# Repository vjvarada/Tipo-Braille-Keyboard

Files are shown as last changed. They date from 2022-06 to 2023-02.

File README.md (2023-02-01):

# What is a Braille KeyPad ?

- Braille KeyPad is a Bluetooth keyboard with a special layout that allows visually impaired individuals to easily navigate and type into SmartPhones and tablets. 
- There are 6 circular Braille input buttons on KeyPad arranged in a braille layout. By pressing combinations of the braille input buttons you can input text and symbols. Braille text input is compliant to UEB Grade 1 and Grade 2 braille except non-ASCII characters and some lower groupsigns & wordsigns.

# Physical Leyout:

- The braille keypads is a rectangular slab with rounded edges. It has all the buttons on one side, and is flat on the other.
- There is a slot for lanyard/wrist straps on one side of the rectangle. 
- Braille KeyPad consists of 6 circular "Braille" keys, 5 square "Special Keys" and a 5-Way Navigation stick with Center click.
- The 6 circular braille keys are used to input text and symbols by brailling in UEB grade 1 and grade 2 braille, in addition to long pressing the braille buttons of certain alphabets to trigger shortcuts on the SmartPhone/Tablet
- The 5 square keys are Alt, Ctrl, Shift, Space & Delete keys.
- The Navigation stick controls up, Down, Left, and Right.
- Clicking the center of the navigation stick represents enter/newline
- The bottom os the device has the ON/OFF slider and the USB Charging input.

# How to use
- Braille KeyPad is held between your palms, with the buttons facing away, and the flat side towards you. 

# Implementation:
How the HID Keypad is implemented for use with Braille

## Grade 1 Braille
The Braille Alphabet—Internationally Standardised
The letters a-z are common and standard for most braille country tables.

Grade 1 braille is a letter-for-letter substitution of its printed counterpart. This is the preferred code for beginners because it allows people to get familiar with, and recognize different aspects of, the code while learning how to read braille. 

English grade 1 braille consists of the 26 standard letters of the alphabet as well as punctuation.
### Charecters

| CHARACTER   |      BRAILLE      |  BRAILLE DOT/BUTTON # |
|----------|:-------------:|------:|
| letter sign | ⠰ | 56|
| a |	    ⠁	    | 1 |
| b |	    ⠃	    | 12 |
| c |	    ⠉	    | 14 |
| d |	    ⠙	    | 145 |
| e |	    ⠑	    | 15 |
| f |	    ⠋	    | 124 |
| g |	    ⠛	    | 1245 |
| h |	    ⠓	    | 125 |
| i |	    ⠊	    | 24 |
| j |	    ⠚	    | 245 |
| k |	    ⠅	    | 13 |
| l |	    ⠇	    | 123 |
| m |	    ⠍	    | 134 |
| n |	    ⠝	    | 1345 |
| o |	    ⠕	    | 135 |
| p |	    ⠏	    | 1234 |
| q |	    ⠟	    | 12345 |
| r |	    ⠗	    |1235 |
| s |	    ⠎	    | 234 |
| t |	    ⠞	    | 2345 |
| u |	    ⠥	    | 136 |
| v |	    ⠧	    | 1236 |
| w |	    ⠺	    | 2456 | 
| x |	    ⠭	    | 1346 |
| y |	    ⠽	    | 13456 |
| z |	    ⠵	    | 1356 |

### Numbers

| CHARACTER   |      BRAILLE      |  BRAILLE DOT/BUTTON # |
|----------|:-------------:|------:|
| number indicator |	⠼ 	| 3456 |
| 1 | 	⠼⠁	| 3456 1 |
| 2 |	⠼⠃	| 3456 12 |
| 3 |	⠼⠉	| 3456 14 |
| 4 |	⠼⠙	| 3456 145 |
| 5 |	⠼⠑	| 3456 15 |
| 6 |	⠼⠋	| 3456 124 |
| 7 |	⠼⠛	| 3456 1245 |
| 8 |	⠼⠓	| 3456 125 |
| 9 |	⠼⠊	| 3456 24 |
| 0 |	⠼⠚	| 3456 245 |

The number indicator (⠼) is placed before the first digit in a group. Space, hyphen, grade 1 indicator or clears it

Example:
```
100: 	⠼⠁⠚⠚

using Grade 1 indicator/Letter sign (⠰) to specify end of number
221b:	⠼⠃⠃⠁⠰⠃

```

### Punctuation

| CHARACTER   |      BRAILLE      |  BRAILLE DOT/BUTTON # |
|----------|:-------------:|------:|
|,|                     ⠂   |2|
|;|                  	⠆   |23|
|:|                    	⠒   |25|
|.(Period)|             ⠲   |256|
|?|     	            ⠦   |236|
|!|                     ⠖   |235|
|apostrophe '|          ⠄   |3|
|quote " |              ⠴   |356|
|hyphen - |             ⠤   |36|

### Symbols

| CHARACTER   |      BRAILLE      |  BRAILLE DOT/BUTTON # |
|----------|:-------------:|------:|
| & |	                 ⠈⠯	    | 4 12346|
| * |	                 ⠐⠔	    | 5 35|
| # |                    ⠸⠹        | 456 1456|
| @	|                    ⠈⠁        | 4 1|
| %	|                    ⠨⠴	    | 46 356|
| +	|                    ⠐⠖	    | 5 235|
| − (minus) |            ⠐⠤	    | 5 36|
| =	|                    ⠐⠶	    | 5 2356|
| ~ |                    ⠈⠔        | 4 35 |
| ` |                    ⠘⠡        | 45 16
| ^ |                    ⠈⠢        |4 26 |
| Underscore _ |         ⠨⠤        |46 36|
| Verical Line |         ⠸⠳        |456 1256| 
| / |                    ⠸⠌        |456 34|
| \ |                    ⠸⠡        |456 16|
| ( |                    ⠐⠣        |5 126|
| ) |                    ⠐⠜        |5 345|
| [ |                    ⠨⠣        |46 126|
| ] |                    ⠨⠜        |46 345|
| { |                    ⠸⠣        |456 126|
| } |                    ⠸⠜        |456 345|
| < |                    ⠈⠣        |4 126|
| > |                    ⠈⠜        |4 345|
| $ |                    ⠈⠎        |4 234 |
| " |                    ⠠⠶        |6 2346 |

### Indicators

| CHARACTER   |      BRAILLE      |  BRAILLE DOT/BUTTON # |
|----------|:-------------:|------:|
| number indicator |                	⠼    	| 3456 |
| grade 1 letter indicator |           ⠰	    | 56|
| grade 1 word indicator |             ⠰⠰	    | 56 56|
| grade 1 lock indicator |             ⠰⠰⠰	    | 56 56|
| grade 1 terminator indicator |       ⠰⠄	    | 56 3|
| capital letter indicator |           ⠠	    | 6|
| capital word indicator |             ⠠⠠      | 6 6|
| capital lock indicator |             ⠠⠠⠠     | 6 6 6|
| capital terminator indicator |       ⠠⠄      | 6 3|

```
The capital(ization) sign ⠠ marks the first letter of a word as capitalized. 
It may occur in the middle of a word for camel case, as in the name deAngelo. 
It is doubled to place a word in all caps; this must be repeated for each word of an all-cap text.
Use ⠠⠠ to Capitalise proceeding charecter, ⠠⠠ to Capitalise a full word,
⠠⠠⠠ to capitalise a full passage and ⠠⠄ to terminate. Using space/hyphen 
etc resets to normal unless not using paragraph caps. 
Warning: ⠠⠺⠁⠗⠝⠊⠝⠛
WARNING: ⠠⠠⠺⠁⠗⠝⠊⠝⠛
```

```
Note: The letter sign (grade 1 symbol indicator) ⠰ is used to force the end of a series of numbers.
For example, ⠙⠁ ⟨da⟩ preceded by a number sign, ⠼⠙⠁, is read as 41. 
If instead 4a is intended (as in a section or apartment number), 
then the letter sign is used to force a reading of a rather than 1 for the final character: ⠼⠙⠰⠁ ⟨4a⟩.

It is also used to mark a character as standing for a letter rather than for a word. For example, ⠃ ⟨b⟩ on its own is normally read as the word but;
to indicate that it is instead the letter b, the letter sign is used: ⠰⠃ b. Plurals of letters (mind your ps and qs)
always use an apostrophe in braille, but other derivations may not, as in ⠰⠝⠹ nth [time]: ⠠⠎⠬ is Sing, ⠰⠠⠎⠬ is S-ing/Essing. The letter sign is also used to mark lower-case Roman numbers, as in ⠰⠊⠊⠊ ⟨iii⟩.
 ```
## Grade 2 Braille 

The literary braille code, grade 2, uses “contractions” that substitute shorter sequences for the full spelling of commonly-occurring letter groups. The contractions are similar to English print contractions, like “cannot” versus “can’t”, in the way that a word is shortened. For example, “the” is usually a single character in braille. 
Grade 2 braille is the most commonly used form of braille code and is found in books, public signage, and restaurant menus to name a few. It consists of the 26 standard letters of the alphabet, punctuation, and contractions.

```
letter sign  (⠰) used to mark a character as standing for a letter rather than for a word. For example,
 ⠃ ⟨b⟩ on its own is normally read as the word but; to indicate that it is instead the letter b, 
the letter sign is used: ⠰⠃ b. Plurals of letters (mind your ps and qs) always use an apostrophe in braille,
but other derivations may not, as in ⠰⠝⠹ nth [time]: ⠠⠎⠬ is Sing, ⠰⠠⠎⠬ is S-ing/Essing.[27] The letter sign 
is also used to mark lower-case Roman numbers, as in ⠰⠊⠊⠊ ⟨iii⟩.
```
### Alphabetic Wordsigns

| CHARACTER   | WORD    |      BRAILLE      |  BRAILLE DOT/BUTTON # |
|----------|:-------------:|:-------------:|------:|
| b | but |	            ⠃	    | 12 |
| c | can |	            ⠉	    | 14 |
| d | do |	            ⠙	    | 145 |
| e | every|            ⠑	    | 15 |
| f | from |            ⠋	    | 124 |
| g | go |              ⠛	    | 1245 |
| h | have |            ⠓	    | 125 |
| j | just |            ⠚	    | 245 |
| k | knowledge |	    ⠅	    | 13 |
| l | like |	        ⠇	    | 123 |
| m | more |	        ⠍	    | 134 |
| n | not |	            ⠝	    | 1345 |
| p | people |	        ⠏	    | 1234 |
| q | quite |	        ⠟	    | 12345 |
| r | rather |	        ⠗	    |1235 |
| s | so |	            ⠎	    | 234 |
| t | that |	        ⠞	    | 2345 |
| u | us |	            ⠥	    | 136 |
| v | very |	        ⠧	    | 1236 |
| w | will |	        ⠺	    | 2456 | 
| x | it |	            ⠭	    | 1346 |
| y | you |	            ⠽	    | 13456 |
| z | as |	            ⠵	    | 1356 |

### Strong Contractions (Part and Whole Word)

| CHARACTER   |      BRAILLE      |  BRAILLE DOT/BUTTON # |
|----------|:-------------:|------:|
| and |	    ⠯	    | 12346 |
| for |	    ⠿	    | 123456 |
| of |	    ⠷	    | 12356 |
| the |	    ⠮	    | 2346 |
| with |    ⠾	    | 23456 |

### Strong Wordsigns

| CHARACTER   |      BRAILLE      |  BRAILLE DOT/BUTTON # |
|----------|:-------------:|------:|
| child |	    ⠡	    | 16 |
| shall |	    ⠩	    | 146 |
| this |	    ⠹	    | 1456 |
| which |	    ⠱	    | 156 |
| out |	        ⠳	    | 1256 |
| still |	    ⠌	    | 34 |

isStandingAlone?

### Strong Groupsigns

| CHARACTER   |      BRAILLE      |  BRAILLE DOT/BUTTON # | Note |
|----------|:-------------:|:------:|------:|
| -ch- |	    ⠡	    | 16 | Letter join on either side|
| -sh- |	    ⠩	    | 146 |Letter join on either side|
| -th- |        ⠹	    | 1456 |Letter join on either side|
| -wh- |	    ⠱	    | 156 |Letter join on either side|
| -ou- |	    ⠳	    | 1256 |Letter join on either side|
| -st- |	    ⠌	    | 34 |Letter join on either side|
|------|----------------|----| -------------------------|
| gh |	        ⠣	    | 126 |
| ed |	        ⠫	    | 1246 |
| er |	        ⠻	    | 12456 |
| ow |          ⠪	    | 246 |
| ar |  	    ⠜	    | 345 |
| -ing |	    ⠬	    | 346 |Letter join on one side only, cannot be used to start a word|

### Lower Groupsigns

| CHARACTER   |      BRAILLE      |  BRAILLE DOT/BUTTON # | Note |
|----------|:-------------:|:------:|------:|
| -ea- |      ⠂	    | 2|Letters join on both side|
| -bb- |      ⠆	    | 23 |Letters join on both side|
| -cc- |      ⠒	    | 25 |Letters join on both side|
| -ff- |	  ⠖	    | 235 |Letters join on both side|
| -gg- |      ⠶	    | 2356 |Letters join on both side|
|------|----------------|----| -------------------------|
| be- |	      ⠆	    | 23 | |
| con- |	  ⠒	    | 25 |Letters join on one side only |
| dis- |	  ⠲	    | 256 |Letters join on one side only |
| -en- |	  ⠢	    | 26 |Letter join on either side|
| in |	      ⠔	    | 35 | |

### Lower Wordsigns

| CHARACTER   |      BRAILLE      |  BRAILLE DOT/BUTTON # |
|----------|:-------------:|------:|
| be |      ⠆	    | 23 |
| enough |  ⠢	    | 26 |
| were |    ⠶	    | 2356 |
| his |	    ⠦	    | 236 |
| in |	    ⠔	    | 35 |
| was |	    ⠴	    | 356 |

### Initial Letter Contractions

| CHARACTER   |      BRAILLE      |  BRAILLE DOT/BUTTON # |
|----------|:-------------:|------:|
|    day |  |5 145
|   ever |  |5 15
|  father | |5 124
|    here | |5 125
|    know | |5 13
|    lord | |5 123
|    mother |   |5 134
|    name | |5 1345
|    one |  |5 135
|    part | |5 1234
|    question | |5 12345
|    right |    |5 1235
|    some | |5 234
|    time | |5 2345
|    under | |5 136
|    work | |5 2456
|    young | |5 13456
|    there | |5 2346
|    character | |5 16
|    through | |5 1456
|    where | |5 156
|    ought | |5 1256
|    upon | |45 136
|    word | |45 2456
|    these | |45 2346
|    those | |45 1456
|    whose | |45 156
|    cannot | |456 14
|    had | |456 125
|    many | |456 134
|    spirit | |456 234
|    world | |456 2456
|    their | |456 2346

### final Letter Groupsigns

| CHARACTER   |      BRAILLE      |  BRAILLE DOT/BUTTON # |
|----------|:-------------:|------:|
|ound| | 46 145 |
|ance| | 46 15 |
|sion| | 46 1345 |
|less| | 46 234|
|ount| | 46 2345|
|ence| | 56 15|
|ong| | 56 1245|
|ful| | 56 123|
|tion| | 56 1345|
|ness| | 56 234|
|ment| | 56 2345|
|ity| | 56 13456|

## Talkback Basics

|Key Combo      |   Action | 
|:----------|------:|
| Hold z | Pause/Resume Talkback | 
| Alt + Space | Open Talkback Menu | 

## Item Navigation controls

|Key Combo      |   Action | 
|:----------|------:|
| Alt + Left  | Navigate to the next item|
| Alt + Right  | Navigate to the previous item |
| Alt + Up | Navigate to the item above |
| Alt + Down | Navigate to the item below|
|_________|________|
| Alt + Ctrl + Left | Navigate to First Item |
| Alt + Ctrl + Right | Navigate to Last Item |
| Alt + Ctrl + Down  | Navigate to Next Window |
| Alt + Ctrl + Up | Navigate to Previous Window |
|_________|________|
| Alt + Enter | Select an item |
| Alt + Shift + Enter |Long press | 

## Text Editing  
|Key Combo      |   Action | 
|:----------|------:|
| Right | Move cursor right |
| Left | Move cursor left |
| Up | Move cursor to line above |
| Down | Move cursor to line below |
| Ctrl + Right | Move cursor to Previous Word |
| Ctrl + Left | Move Cursor to Next Word |
| Shift + Right | Select next character |
| Shift + Left | Select Previous Character |
| Shift + Up | Select Line Above |
| Shift + Down | Select Line Below |
| Shift + Ctrl + Left | Select Previous Word |
| Shift + Ctrl + Right | Select Next Word |

## Reading controls

|Key Combo      |   Action | 
|:----------|------:|
| Alt + Shift + Control + Up/Down | Cycle Reading Controls | 
| Alt + Shift + Up/Down | Go to Next/Prev as per reading Controls |
| Alt + Shift + Right  | Navigate to Next Character |
| Alt  + Shift + Left |  Navigate to Previous Character |
| Alt + Ctrl + Shift + Right | Navigate to Next Word |
| Alt + Ctrl + Shift + Left |  Navigate to Previous Word |

## Continuous Reading controls

|Key Combo      |   Action | 
|:----------|------:|
| Alt + Ctrl + Enter | Continuous read from top |
| Alt + Ctrl + Shift + Enter | Continuous read from Next Item |
| Alt + Right  | Fast-forwards the text.|
| Alt + Left | Rewinds the text. |
| Enter | Stop Continuous Reading |

## Slider Controls  

|Key Combo      |   Action | 
|:----------|------:|
| Alt + Shift + Up | Increase Slider Value|
| Alt + Shift + Down  | Decrease Slider Value |

## Alphabetic Shortcuts

Long press braille character to activate

| CHARACTER   |      Shortcut      |  Key Combo |
|----------|:-------------:|------:|
| a | Assistant | win |
| b | Back | alt + backspace |
| l | Apps List / Select All | Ctrl + a |
| c | Copy | ctrl + c |
| x | Cut | ctrl + x |
| v | Paste | ctrl + v |
| d | Maps | win + m |
| e | Email | win + e |
| h | Home | ctrl + alt + h |
| r | Recent apps | ctrl + alt + r |
| s | Music | win + p |
| m | Messages | win + s |
| n | notifications | ctrl + alt + n |
| f | Screen Search | ctrl + alt + / |
| p | Contacts | win + c |
| y | Youtube | win + y |
| t | Calender | win + l |

#### References:

1. Generate Markdwn tables from https://www.tablesgenerator.com/markdown_tables
2. Braille Code Referance: https://www.pharmabraille.com/braille-codes/unified-english-braille-ueb-code/
3. Test and understand using online braille translator: https://www.branah.com/braille-translator
4. Wikipedia entry https://en.wikipedia.org/wiki/English_Braille
5. http://www.dotlessbraille.org/brailleindicators.htm#markup
6. Android & TalkBack Mobile Accessibility Cheat Sheet https://pauljadam.com/demos/talkbackcheatsheet.html
7. Keyboard Shortcuts https://www.cnet.com/culture/keyboard-shortcuts-for-android-phones/
8. Talkback Shortcuts https://dequeuniversity.com/screenreaders/talkback-shortcuts
9. Braille to Binary encoder https://www.dcode.fr/braille-alphabet

# TIPO
Plug n Play Braille Keyboard for your smartphone
Shows up as a HID device, and behaves just like a Keyboard would.

## TIPO V1
USB HID only implementation using atmega32u4/Adruni Leonardo

## TIPO BLE

BLE HID implementation using ESP32

------------------------------------------------------------------
# Hardware Connections

## Architecture
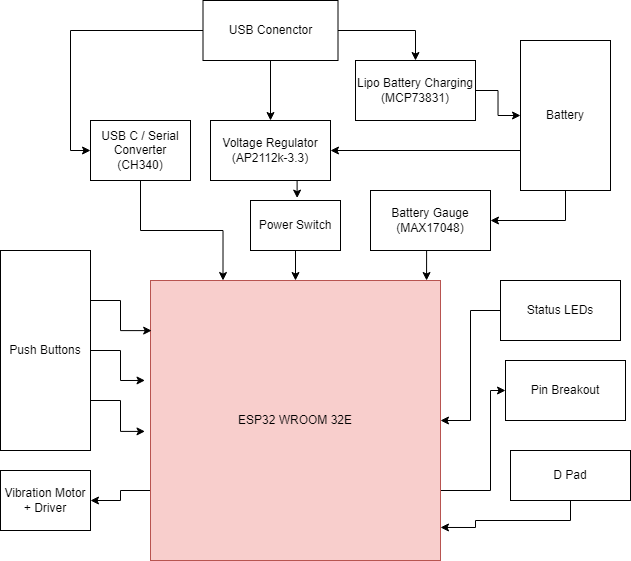
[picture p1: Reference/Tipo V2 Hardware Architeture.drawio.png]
Hardware Architecture


## Button Map:

| Button | ESP32 Pin # |
| :------: | :-----------:|
| BTN1 | 25|
| BTN2 | 26|
| BTN3 | 27|
| BTN4 | 13|
| BTN5 | 15|
| BTN6 | 2 |
| BTN7 | 19|
| BTN8 | 18|
| BTN9 | 17|
| BTN10| 16|
| BTN11| 4 |
| CNT | 33|
| UP | 34 |
| DWN | 35|
| LFT | 36|
| RGT | 39|

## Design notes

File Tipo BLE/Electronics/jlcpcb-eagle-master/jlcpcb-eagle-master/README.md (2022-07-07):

# jlcpcb-eagle
EAGLE cad helpers for JLCPCB (https://jlcpcb.com) production and assembly services

## General info

Rules and scripts have been tested under EAGLE cad 9.5.

They're provided AS IS, with no warranty. Any feedback is greatly appreciated and
can be provided via issue tickets.

### Installation

Copy each file in their respective folders (USER_HOME/Documents/EAGLE/).

## CAM jobs

The details of these CAM jobs are covered in article [How to Generate Gerber and Drill Files in Autodesk Eagle](https://support.jlcpcb.com/article/137-how-to-generate-gerber-and-drill-files-in-autodesk-eagle), so they must be used together.

The jobs follow the naming guidelines defined here: https://support.jlcpcb.com/article/29-suggested-naming-patterns

They also include tCream/bCream solderpaste layers that could be used for the stencil service.

### Eagle 8.6.0 to 9.6.2

* cam/jlcpcb_2_layer_v9.cam : For 2-layer boards
* cam/jlcpcb_4_layer_v9.cam : For 4-layer boards
* cam/jlcpcb_6_layer_v9.cam : For 6-layer boards

### Eagle 7.2 to 8.5.2

* cam/jlcpcb_2_layer_v72.cam : For 2-layer boards
* cam/jlcpcb_4_layer_v72.cam : For 4-layer boards
* cam/jlcpcb_6_layer_v72.cam : For 6-layer boards

### Eagle 7.1 and Lower

For Eagle 5, 6 and 7.1

* cam/jlcpcb_2_layer_v6.cam : For 2-layer boards
* cam/jlcpcb_4_layer_v6.cam : For 4-layer boards
* cam/jlcpcb_6_layer_v6.cam : For 6-layer boards

## Design rules

* design rules/jlcpcb-2layers.dru: 2-layers version, 35u copper, 1.6mm board thickness

Mainly based on EAGLE's standard design rules, it adds the declared JLCPCB's capabilities listed
here: https://jlcpcb.com/capabilities/Capabilities

Note: annular ring for pads aren't minimal, in order to allow proper solderability of TH components

## ULPs

### BOM/CPL Exporter

* BOM: Bill of Materials
* CPL: Component Placement List (i.e. Pick and Place file)

The smta exporter ULP can be used to quicken the process of creating the required files for the SMT assembly service.

#### Files

* ulps/jlcpcb_smta_exporter.ulp: For Eagle 9
* ulps/jlcpcb_smta_exporter_v7.ulp: Tested in Eagle 7.7.0

#### Usage

Observe the following:

1. it must be executed from the board editor
2. it asks for the layer to process (either top or bottom), this must be consistent with the ordering process
3. it asks for a directory where to export the two files
4. the two files will be named ```<boardname>_<side>_bom.csv``` and ```<boardname>_<side>_cpl.csv```
5. components rotations are sketchy and must be visually checked on the online gerber viewer once uploaded the files

The ULP can extract LCSC part ordering numbers from the packages attributes. The attribute must be named _LCSC_PART_ or _LCSC_ and it should contain the order code found in the parts library https://jlcpcb.com/parts (eg: C25804).

The ULP can also manually rotate the angle in the CPL output file. The attribute must be named _JLC_ROTATION_ or _JLC_ROT_. For example, if a part's angle in set to 90 and it's attribute _JLC_ROTATION_ is set to 180, the angle in the final CPL file will be set to 270.

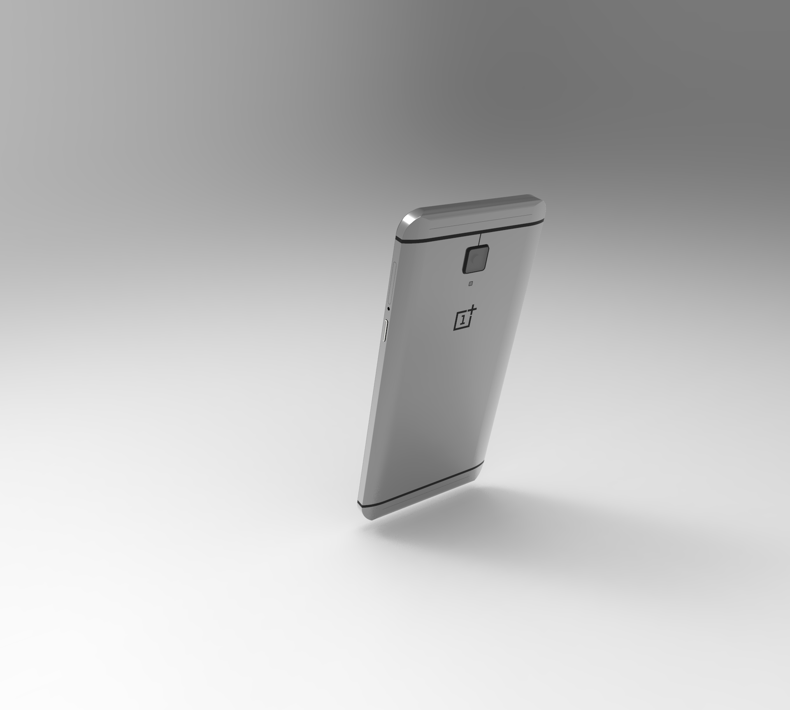
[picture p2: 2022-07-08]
Tipo BLE/Design/BLE V2 Design/oneplus3t-1.snapshot.2/op3t/untitled.27.jpg

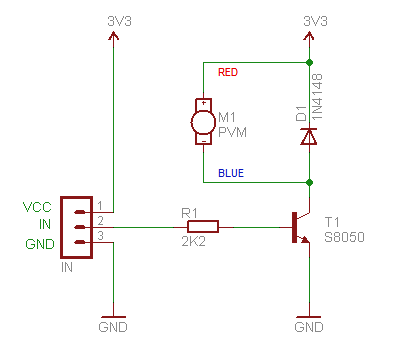
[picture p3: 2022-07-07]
Tipo BLE/Electronics/Datasheets/screenshot-www.electronicsforu.com-2022.07.05-18_01_15.png

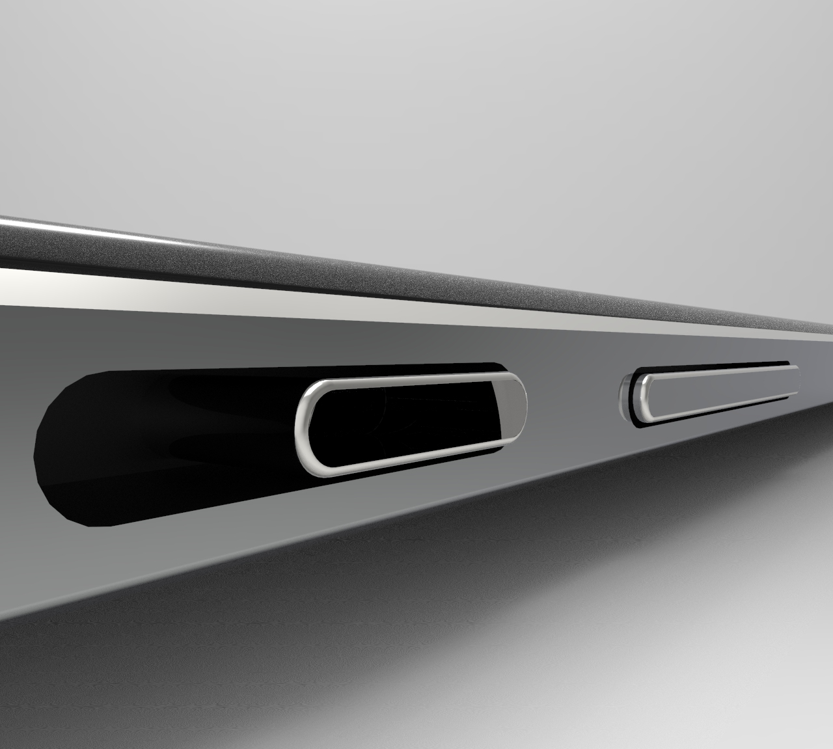
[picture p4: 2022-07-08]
Tipo BLE/Design/BLE V2 Design/oneplus3t-1.snapshot.2/op3t/untitled.25.jpg

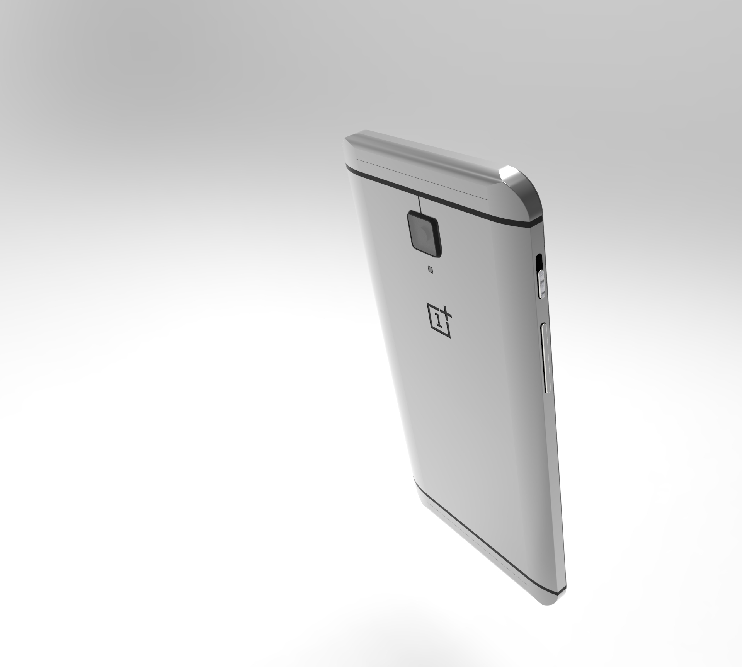
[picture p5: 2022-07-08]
Tipo BLE/Design/BLE V2 Design/oneplus3t-1.snapshot.2/op3t/untitled.30.jpg

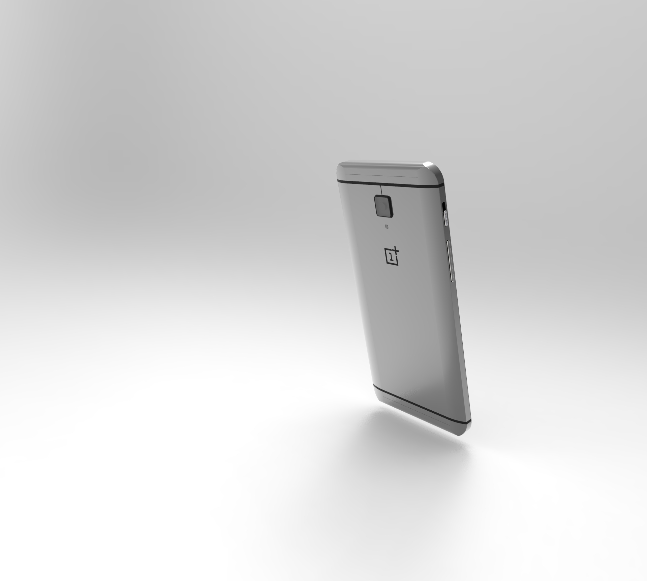
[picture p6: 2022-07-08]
Tipo BLE/Design/BLE V2 Design/oneplus3t-1.snapshot.2/op3t/untitled.28.jpg

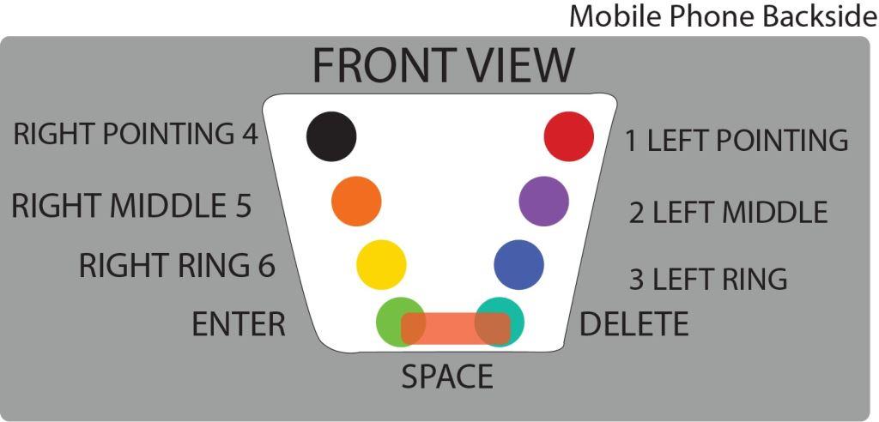
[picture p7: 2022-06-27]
Tipo V1/Design/Layout.jpg

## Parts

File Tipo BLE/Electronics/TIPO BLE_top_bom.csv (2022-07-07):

Comment | Designator | Footprint | LCSC Part #
C95872 | D2 | DO-214AC
918-418K2023S40001 | J1 | USB-C-16P-2LAYER-PADS
0.1uF | C2 C15 | 0402-TIGHT
1.0uF | C7 C10 | 0402-TIGHT
1k | R3 R4 R34 | 0402-TIGHT
2.0k | R6 | 603
2.2k | R1 | 603
3A/10V/280mV | D4 | SOD-323
4.7uF | C6 | 0402-TIGHT
4.7uF | C19 | 603
5.1k | R9 R10 | 0402-TIGHT
10k | R2 R5 R7 R8 R11 R12 R13 R17 R18 | 0402-TIGHT
10uF | C1 | 0402-TIGHT
20V/4.2A/52mΩ/1.4W | Q3 | SOT23-3
AP2112K-3.3 | U3 | SOT23-5
BLUE | D3 | LED-0603
Boot | S3 | TACTILE_SWITCH_SMD_4.6X2.8MM
CH340C | U7 | SO016
ESP-WROOM-32NARROW | U2 | ESP-WROOM-32-NARROW
MAX17048 | U4 | DFN-8
MBT3904DW1T1 | Q2 | SC70-6
MCP73831 | U1 | SOT23-5
RED | D12 | LED-0603
Reset | S4 | TACTILE_SWITCH_SMD_4.6X2.8MM
SS8050 | T1 | SOT23
Yellow | D1 | LED-0603

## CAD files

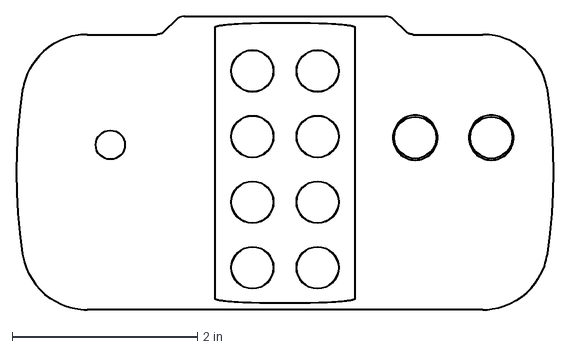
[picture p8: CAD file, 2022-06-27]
Tipo BLE/Design/BLE V1 Design/Tipo BLE dimention.dxf
5.80 x 3.17 in

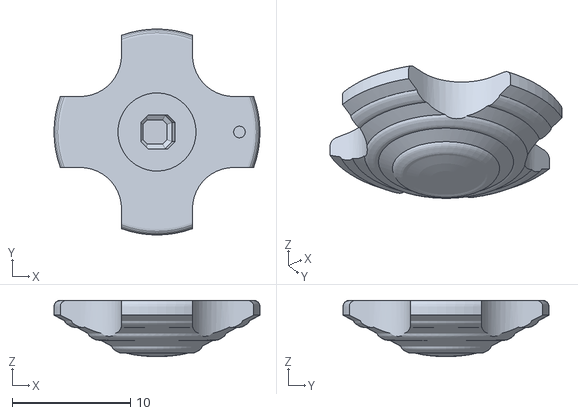
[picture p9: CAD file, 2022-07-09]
Tipo BLE/Design/BLE V2 Design/JOtstick.stl
17.4 x 17.4 x 4.75

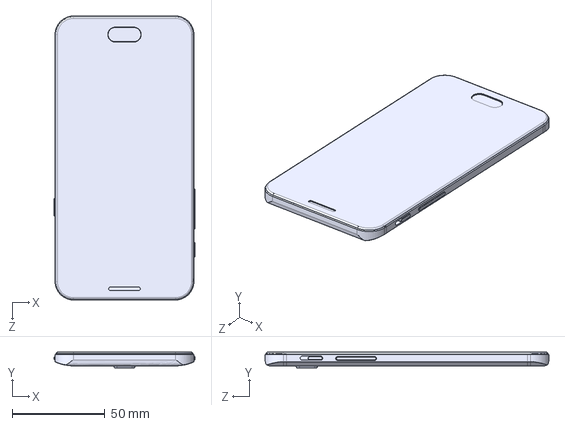
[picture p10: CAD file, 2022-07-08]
Tipo BLE/Design/BLE V2 Design/oneplus3t-1.snapshot.2/OnePlus3T_sagar.IGS
75.7 x 8.40 x 152.7 mm

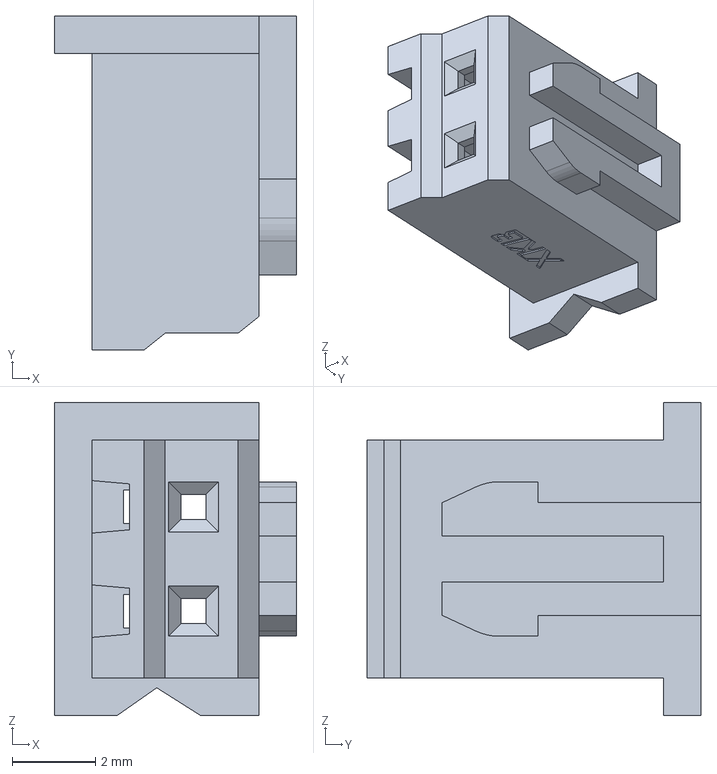
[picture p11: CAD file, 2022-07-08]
Tipo BLE/Design/BLE V2 Design/PCB Components/128261816-3-x8821h-02-n0/X8821H-02-N0.stp
5.80 x 8.00 x 7.50 mm

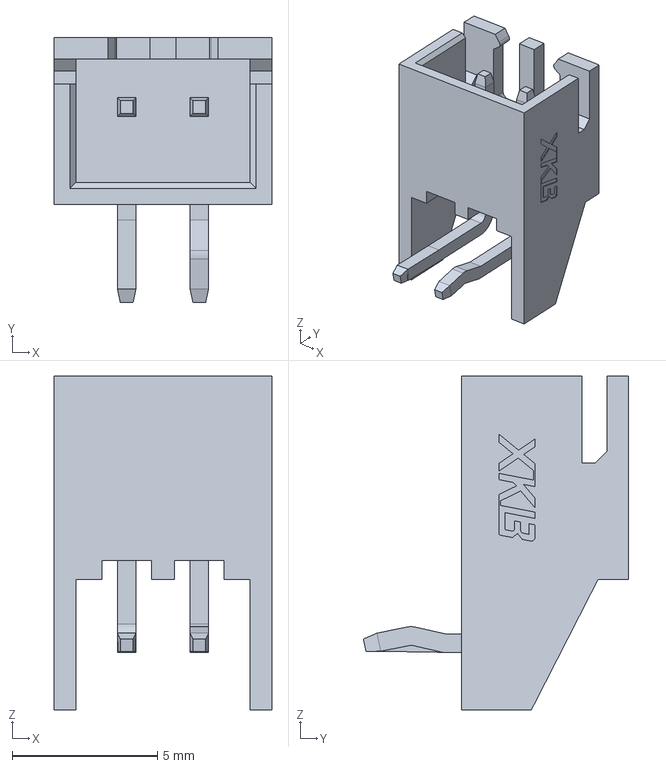
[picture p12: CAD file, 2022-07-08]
Tipo BLE/Design/BLE V2 Design/PCB Components/128261855-3-x8821wr-02k-n2sn/X8821WR-02K-N2SN.stp
7.50 x 9.14 x 11.5 mm

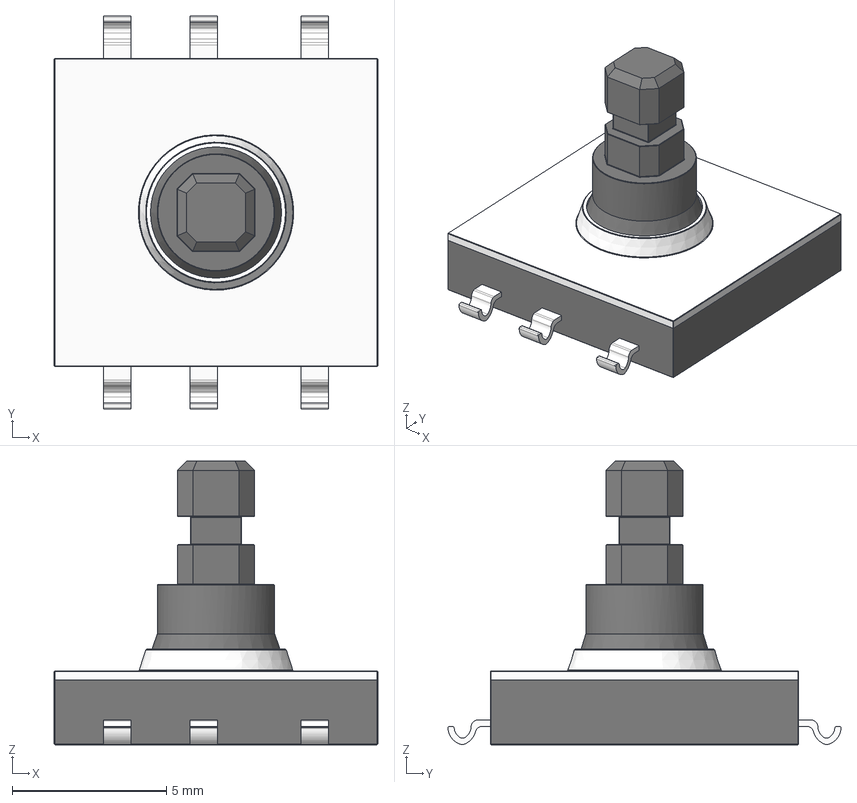
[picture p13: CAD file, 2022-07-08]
Tipo BLE/Design/BLE V2 Design/PCB Components/5-way-tactile-button-smd-1.snapshot.1/5-WayTactileButton10mmSMD.stp
10.5 x 12.8 x 9.20 mm

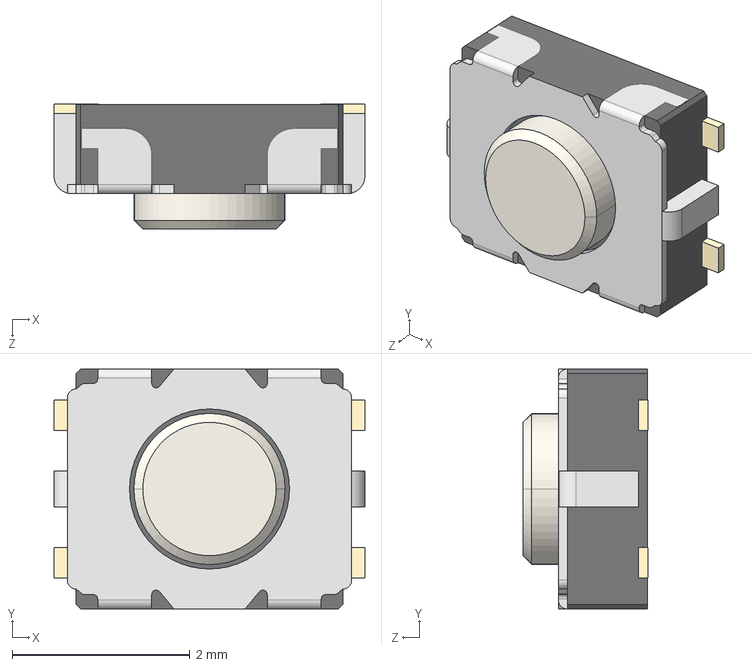
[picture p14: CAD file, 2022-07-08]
Tipo BLE/Design/BLE V2 Design/PCB Components/alpsalpine-sksgpce010-1.snapshot.2/ALPSALPINE SKSGPCE010.STEP
3.50 x 2.70 x 1.41 mm

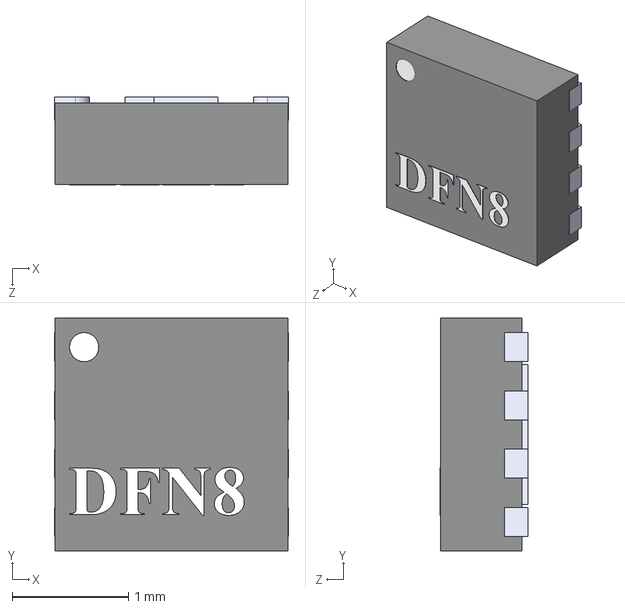
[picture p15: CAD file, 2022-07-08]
Tipo BLE/Design/BLE V2 Design/PCB Components/dfn8-2x2mm-1.snapshot.1/DFN8_2x2.STEP
2.01 x 2.00 x 0.755 mm

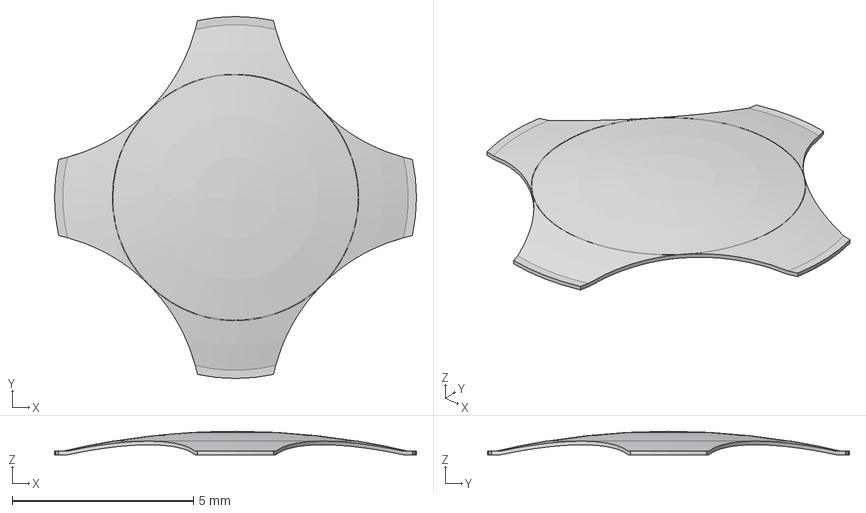
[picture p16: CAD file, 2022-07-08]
Tipo BLE/Design/BLE V2 Design/PCB Components/metal-dome-press-button-1.snapshot.1/Keystone10mmDiaDomePB v2.step
10.0 x 10.0 x 0.65 mm

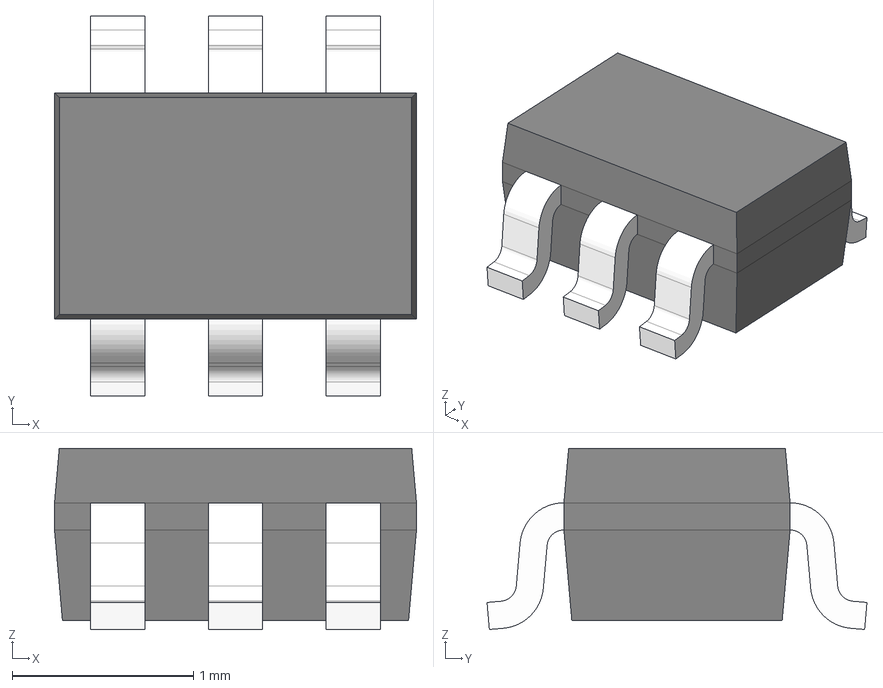
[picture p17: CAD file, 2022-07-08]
Tipo BLE/Design/BLE V2 Design/PCB Components/SC70-6L_82400274.step
2.00 x 2.10 x 1.00 mm

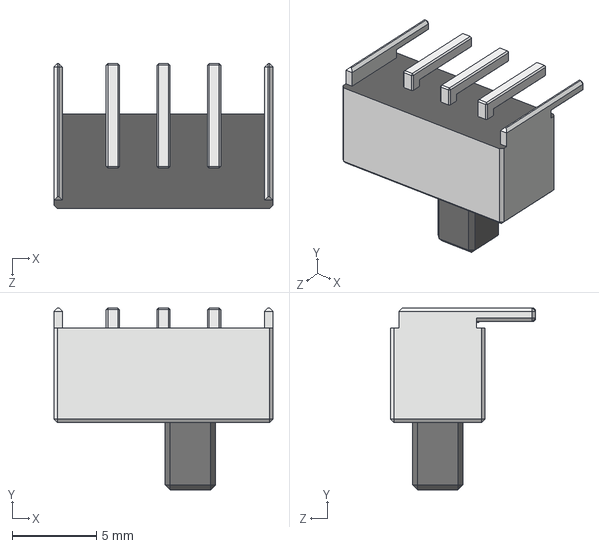
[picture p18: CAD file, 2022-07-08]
Tipo BLE/Design/BLE V2 Design/PCB Components/ss-8-slide-switch-1.snapshot.1/SS-8.step
13.0 x 10.8 x 8.60 mm

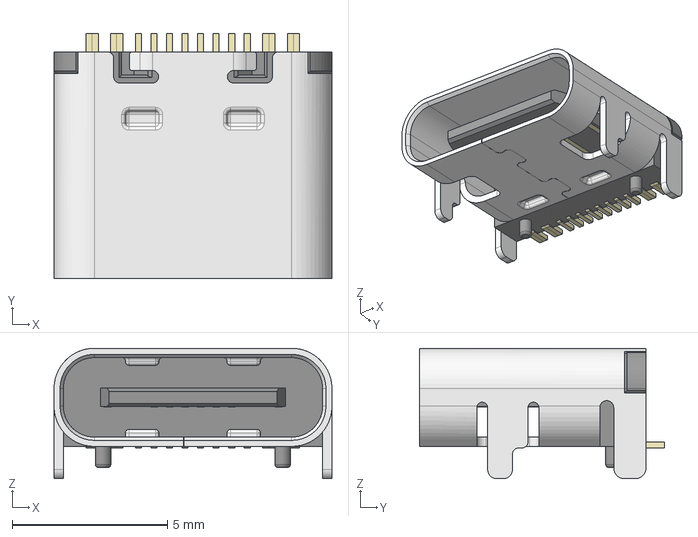
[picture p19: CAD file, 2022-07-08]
Tipo BLE/Design/BLE V2 Design/PCB Components/type-c-31-m-12-1.snapshot.5/HRO_TYPE-C-31-M-12.step
8.95 x 7.90 x 4.20 mm

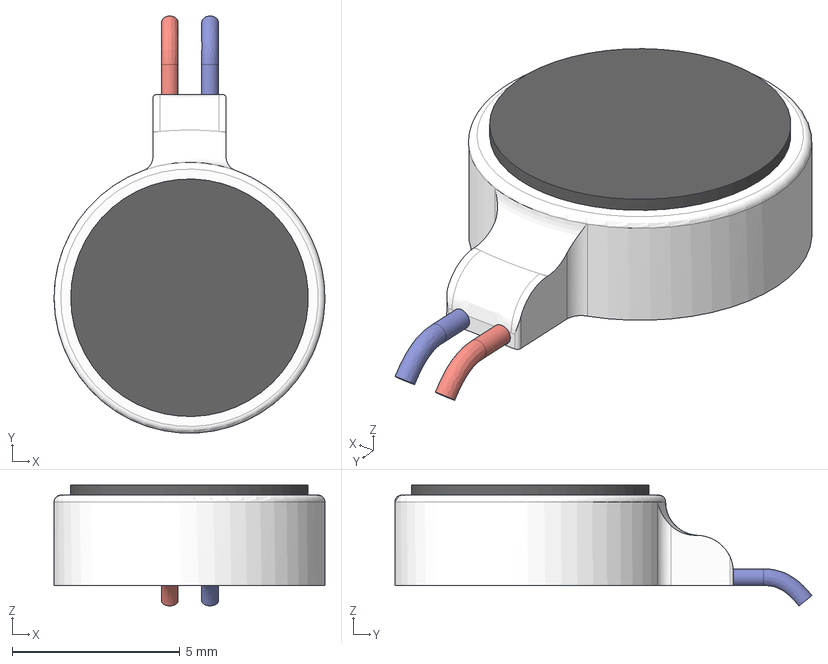
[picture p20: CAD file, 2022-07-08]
Tipo BLE/Design/BLE V2 Design/PCB Components/vibration-motor-7.snapshot.2/Vibration Motor v1.step
8.08 x 12.4 x 3.61 mm

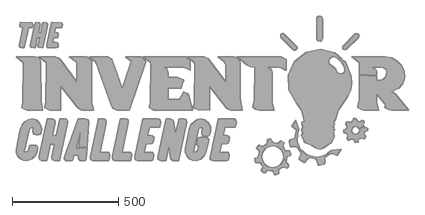
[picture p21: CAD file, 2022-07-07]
Tipo BLE/Design/Logos & Assets/Inventor Challenege.dxf
1852.2 x 748.2

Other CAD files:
Tipo BLE/Design/BLE V2 Design/oneplus3t-1.snapshot.2/op3t/OnePlus3T_sagar.SLDPRT
Tipo BLE/Design/Untitled v0.stl
Tipo BLE/Design/BLE V1 Design/Clampshell Body Top.stl
Tipo BLE/Design/BLE V2 Design/Dome switch retainer.stl
Tipo BLE/Design/BLE V1 Design/Button Head.ipt
Tipo BLE/Design/BLE V1 Design/Clampshell Body Top.ipt
Tipo BLE/Design/BLE V1 Design/ESP.ipt
Tipo BLE/Design/BLE V1 Design/Omron 12x12 button (1).ipt
Tipo BLE/Design/BLE V1 Design/Omron 12x12 button (1).stp
Tipo BLE/Design/BLE V1 Design/Tipo BLE Assembly.iam
Tipo BLE/Design/BLE V1 Design/back cover.ipt
Tipo BLE/Design/BLE V1 Design/back cover.stl
Tipo BLE/Design/BLE V1 Design/joystick.ipt
Tipo BLE/Design/BLE V1 Design/perfboard.ipt
Tipo BLE/Design/BLE V2 Design/Back cover.stl
Tipo BLE/Design/BLE V2 Design/PCB Component.stl
Tipo BLE/Design/BLE V2 Design/PCB Components/LED 0603 Green v1.step
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

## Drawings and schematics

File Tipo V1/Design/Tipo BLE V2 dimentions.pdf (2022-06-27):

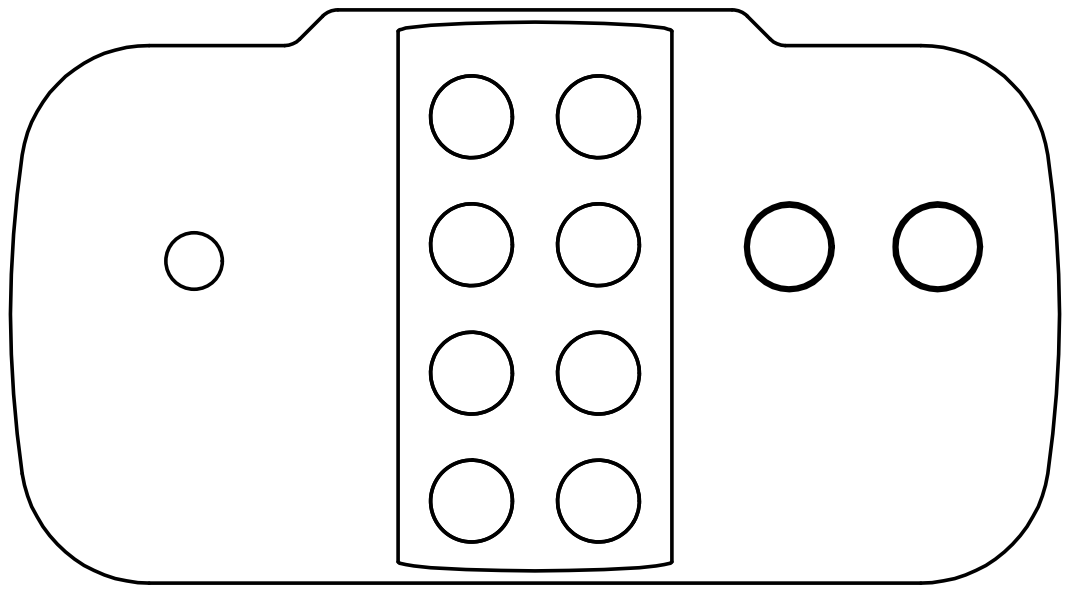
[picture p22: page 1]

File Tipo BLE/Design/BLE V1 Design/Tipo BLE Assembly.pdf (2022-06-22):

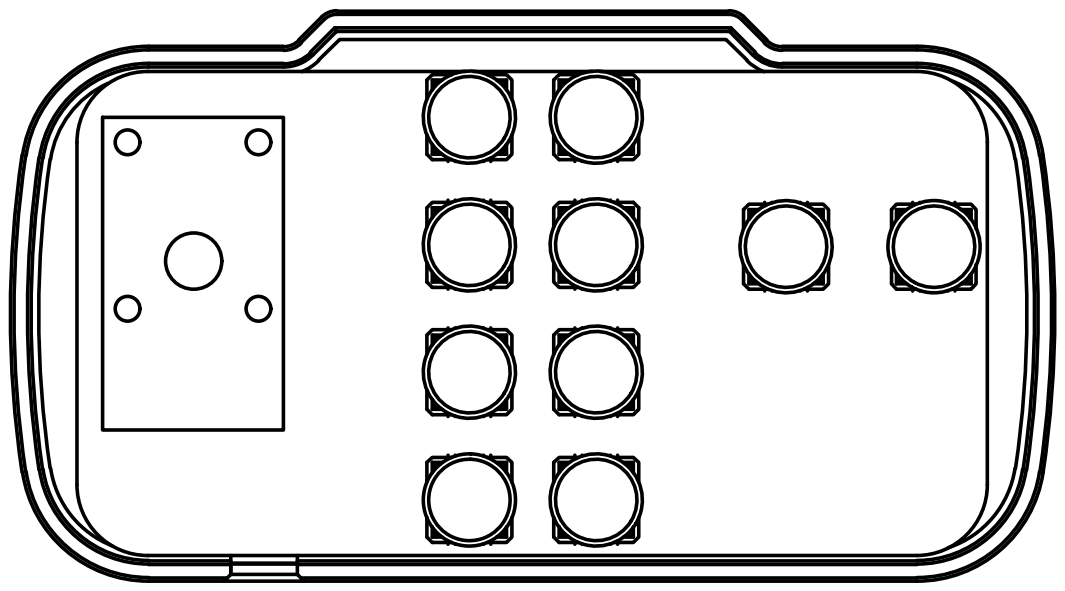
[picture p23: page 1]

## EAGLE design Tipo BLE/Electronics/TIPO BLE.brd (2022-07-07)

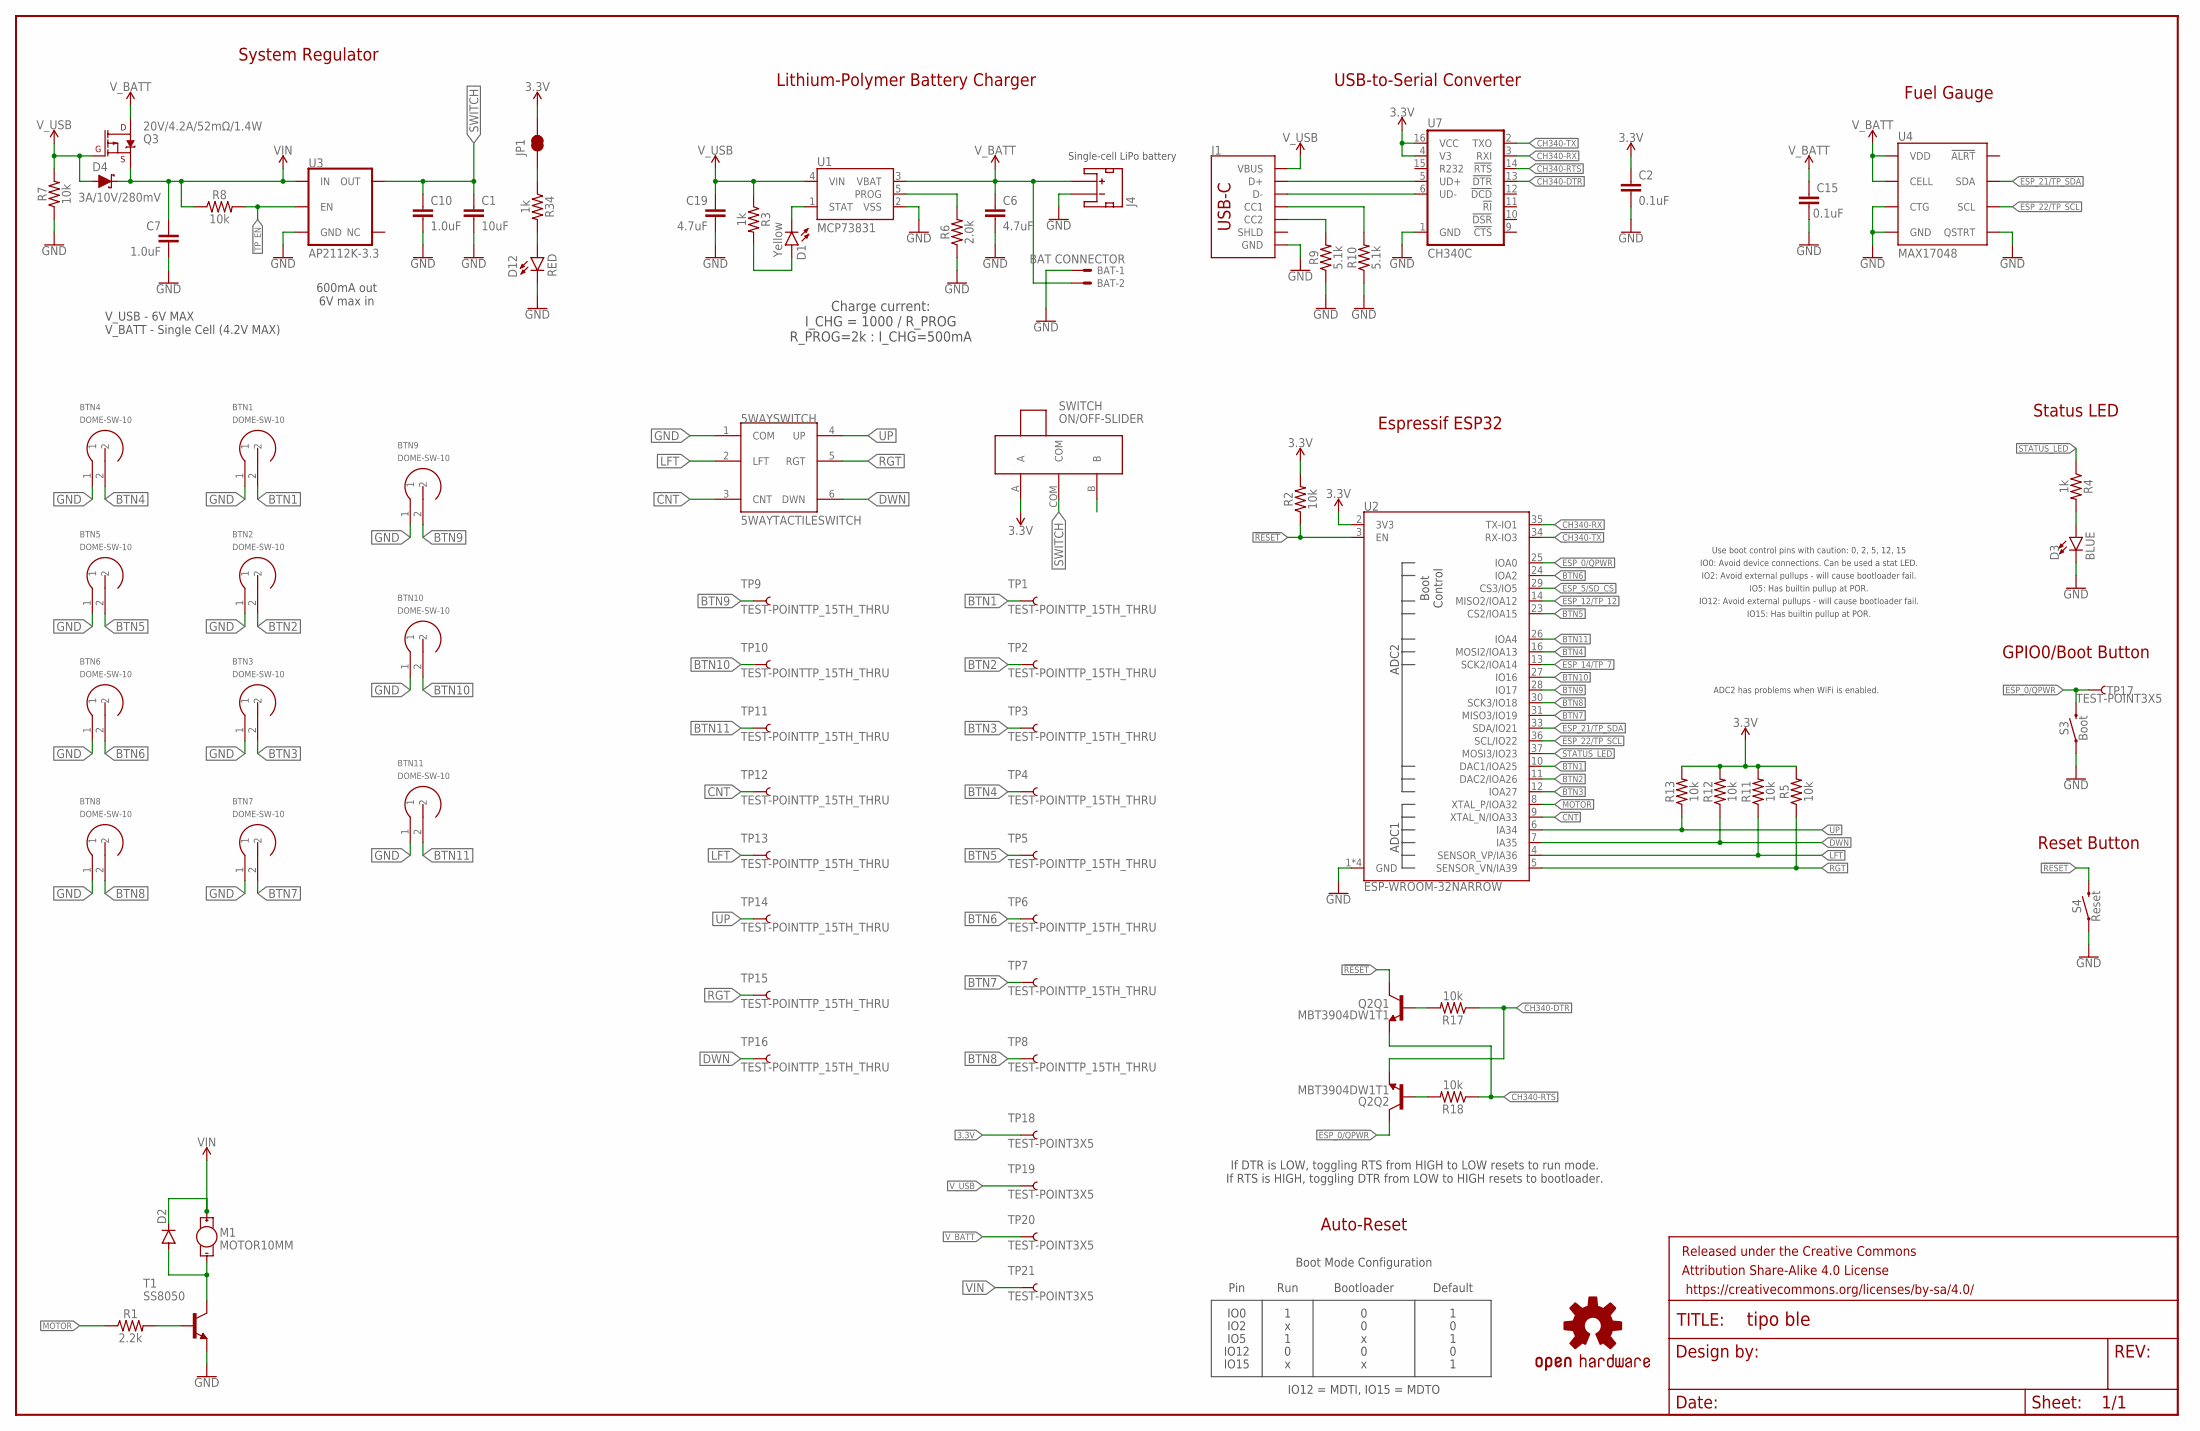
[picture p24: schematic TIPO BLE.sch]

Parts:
5WAYSWITCH: 5WAYTACTILESWITCH
BAT: BAT CONNECTOR; JST-XH-02-PACKAGE-LONG-PAD
BTN1, BTN2, BTN3, BTN4, BTN5, BTN6, BTN7, BTN8, BTN9, BTN10, BTN11: DOME-SW-10
C1: 10uF; 0402-TIGHT
C2, C15: 0.1uF; 0402-TIGHT
C6: 4.7uF; 0402-TIGHT
C7, C10: 1.0uF; 0402-TIGHT
C19: 4.7uF; 0603
D1: Yellow; LED-0603
D2: DIODE-DO-214AC; DO-214AC
D3: BLUE; LED-0603
D4: 3A/10V/280mV; SOD-323
D12: RED; LED-0603
FRAME1: FRAME-LEDGER; CREATIVE_COMMONS
J1: USB_C_2-LAYER_PADS; USB-C-16P-2LAYER-PADS
J4: JST_2MM_MALE; JST-2-SMD@1
JP1: JUMPER-SMT_2_NC_TRACE_SILK; SMT-JUMPER_2_NC_TRACE_SILK
LOGO1: OSHW-LOGOL; OSHW-LOGO-L
M1: MOTOR10MM; VIBE-MOTOR-10MM
Q2: MBT3904DW1T1; SC70-6
Q3: 20V/4.2A/52mΩ/1.4W; SOT23-3
R1: 2.2k; 0603
R2, R5, R7, R8, R11, R12, R13, R17, R18: 10k; 0402-TIGHT
R3, R4, R34: 1k; 0402-TIGHT
R6: 2.0k; 0603
R9, R10: 5.1k; 0402-TIGHT
S3: Boot; TACTILE_SWITCH_SMD_4.6X2.8MM
S4: Reset; TACTILE_SWITCH_SMD_4.6X2.8MM
SWITCH: ON/OFF-SLIDER
T1: SS8050; SOT23
TP1, TP2, TP3, TP4, TP5, TP6, TP7, TP8, TP9, TP10, TP11, TP12, TP13, TP14, TP15, TP16: TEST-POINTTP_15TH_THRU; TP_15TH
TP17, TP18, TP19, TP20, TP21: TEST-POINT3X5; PAD.03X.05
U1: MCP73831; SOT23-5
U2: ESP-WROOM-32NARROW; ESP-WROOM-32-NARROW
U3: AP2112K-3.3; SOT23-5
U4: MAX17048; DFN-8
U7: CH340C; SO016

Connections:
3.3V: C2.1, JP1.2, R2.2, R5.2, R11.2, R12.2, R13.2, SWITCH.A, TP18.1, U2.2 (3V3), U7.4 (V3), U7.16 (VCC)
!RESET!: Q2.3 (C), R2.1, S4.3 (2), S4.4 (2), U2.3 (EN)
BTN1: BTN1.2, TP1.1, U2.10 (DAC1/IOA25)
BTN2: BTN2.2, TP2.1, U2.11 (DAC2/IOA26)
BTN3: BTN3.2, TP3.1, U2.12 (IOA27)
BTN4: BTN4.2, TP4.1, U2.16 (MOSI2/IOA13)
BTN5: BTN5.2, TP5.1, U2.23 (CS2/IOA15)
BTN6: BTN6.2, TP6.1, U2.24 (IOA2)
BTN7: BTN7.2, TP7.1, U2.31 (MISO3/IO19)
BTN8: BTN8.2, TP8.1, U2.30 (SCK3/IO18)
BTN9: BTN9.2, TP9.1, U2.28 (IO17)
BTN10: BTN10.2, TP10.1, U2.27 (IO16)
BTN11: BTN11.2, TP11.1, U2.26 (IOA4)
CH340-DTR: Q2.1 (E), R17.1, U7.13 (!DTR)
CH340-RTS: Q2.4 (E), R18.1, U7.14 (!RTS)
CH340-RX: U2.35 (TX-IO1), U7.3 (RXI)
CH340-TX: U2.34 (RX-IO3), U7.2 (TXO)
CHG: D1.C, U1.1 (STAT)
CHG_LED: D1.A, R3.2
CNT: 5WAYSWITCH.3 (CNT), TP12.1, U2.9 (XTAL_N/IOA33)
D+: J1.A6 (D+), J1.B6 (D+), U7.5 (UD+)
D-: J1.A7 (D-), J1.B7 (D-), U7.6 (UD-)
DTR-10K: Q2.5 (B), R17.2
DWN: 5WAYSWITCH.6 (DWN), R12.1, TP16.1, U2.7 (IA35)
ESP_0/QPWR: Q2.6 (C), S3.3 (2), S3.4 (2), TP17.1, U2.25 (IOA0)
ESP_5/SD_CS: U2.29 (CS3/IO5)
ESP_12/TP_12: U2.14 (MISO2/IOA12)
ESP_14/TP_7: U2.13 (SCK2/IOA14)
ESP_21/TP_SDA: U2.33 (SDA/IO21), U4.8 (SDA)
ESP_22/TP_SCL: U2.36 (SCL/IO22), U4.7 (SCL)
GND: 5WAYSWITCH.1 (COM), BAT.1, BTN1.1, BTN2.1, BTN3.1, BTN4.1, BTN5.1, BTN6.1, BTN7.1, BTN8.1, BTN9.1, BTN10.1, BTN11.1, C1.2, C2.2, C6.2, C7.2, C10.2, C15.2, C19.2, D3.C, D12.C, J1.GND, J1.GND2 (GND), J4.1 (-), R6.1, R7.1, R9.1, R10.1, S3.1, S3.2 (1), S4.1, S4.2 (1), T1.2 (E), U1.2 (VSS), U2.1 (GND), U2.15 (GND), U2.38 (GND), U2.GND, U3.2 (GND), U4.1 (CTG), U4.4 (GND), U4.6 (QSTRT), U4.9 (GND), U7.1 (GND)
LFT: 5WAYSWITCH.2 (LFT), R11.1, TP13.1, U2.4 (SENSOR_VP/IA36)
MOTOR: R1.1, U2.8 (XTAL_P/IOA32)
unnamed: R1.2, T1.1 (B)
unnamed: D2.A, M1.-, T1.3 (C)
unnamed: JP1.1, R34.1
unnamed: J1.B5 (CC2), R9.2
unnamed: J1.A5 (CC1), R10.2
unnamed: D3.A, R4.2
unnamed: R6.2, U1.5 (PROG)
unnamed: D12.A, R34.2
RGT: 5WAYSWITCH.5 (RGT), R5.1, TP15.1, U2.5 (SENSOR_VN/IA39)
RTS-10K: Q2.2 (B), R18.2
STATUS_LED: R4.1, U2.37 (MOSI3/IO23)
SWITCH: C1.1, C10.1, SWITCH.COM, U3.5 (OUT)
TP_EN: R8.2, U3.3 (EN)
UP: 5WAYSWITCH.4 (UP), R13.1, TP14.1, U2.6 (IA34)
VIN: C7.1, D2.C, D4.C, M1.+, Q3.2 (S), R8.1, TP21.1, U3.1 (IN)
V_BATT: BAT.2, C6.1, C15.1, J4.2 (+), Q3.3 (D), TP20.1, U1.3 (VBAT), U4.2 (CELL), U4.3 (VDD)
V_USB: C19.1, D4.A, J1.VBUS1 (VBUS), J1.VBUS2 (VBUS), Q3.1 (G), R3.1, R7.2, TP19.1, U1.4 (VIN)

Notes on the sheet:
System Regulator
600mA out 6V max in
V_USB - 6V MAX V_BATT - Single Cell (4.2V MAX)
Single-cell LiPo battery
Charge current: I_CHG = 1000 / R_PROG R_PROG=2k : I_CHG=500mA
Lithium-Polymer Battery Charger
USB-to-Serial Converter
Fuel Gauge
Reset Button
Status LED
GPIO0/Boot Button
Auto-Reset
Espressif ESP32
If DTR is LOW, toggling RTS from HIGH to LOW resets to run mode. If RTS is HIGH, toggling DTR from LOW to HIGH resets to bootloader.
Pin
IO0
IO2
IO12
IO15
IO5
Run
Bootloader
Default
IO12 = MDTI, IO15 = MDTO
Boot Mode Configuration
IO0: Avoid device connections. Can be used a stat LED.
ADC2 has problems when WiFi is enabled.
IO12: Avoid external pullups - will cause bootloader fail.
Use boot control pins with caution: 0, 2, 5, 12, 15
IO2: Avoid external pullups - will cause bootloader fail.
IO15: Has builtin pullup at POR.
IO5: Has builtin pullup at POR.

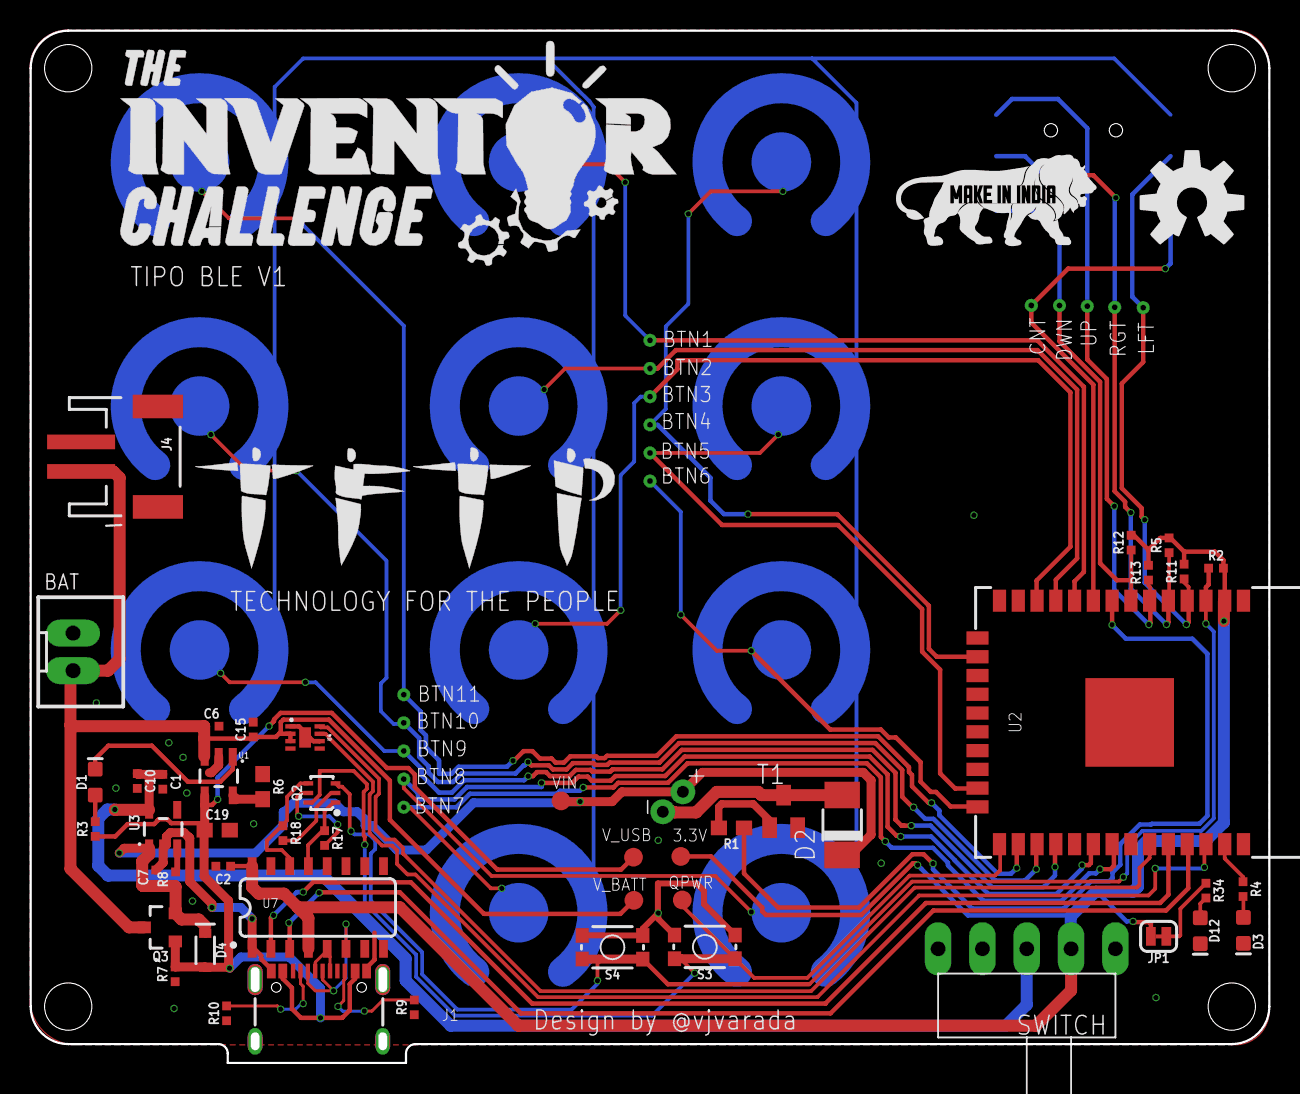
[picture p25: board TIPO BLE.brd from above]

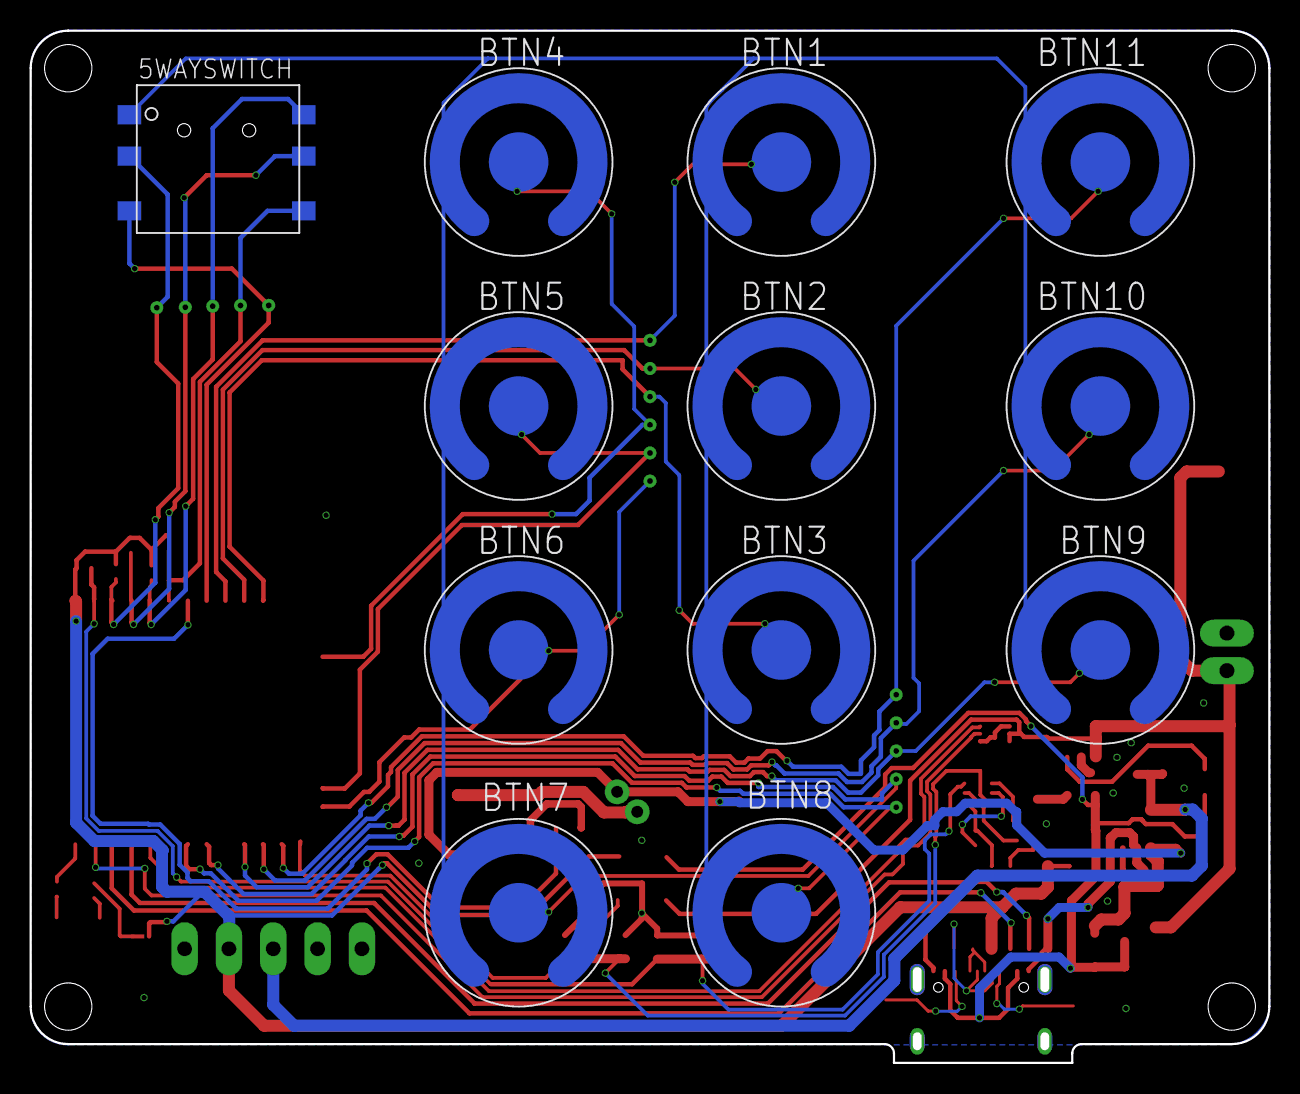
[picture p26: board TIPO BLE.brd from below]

Board: 2 copper layers, 83.8 x 69.8 mm, 82 parts (28 on the bottom side), 47 nets.

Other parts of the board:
U$1: TFTPLOGO
U$2: INVENTORCHALLENGE
U$3: MAKEININDIA

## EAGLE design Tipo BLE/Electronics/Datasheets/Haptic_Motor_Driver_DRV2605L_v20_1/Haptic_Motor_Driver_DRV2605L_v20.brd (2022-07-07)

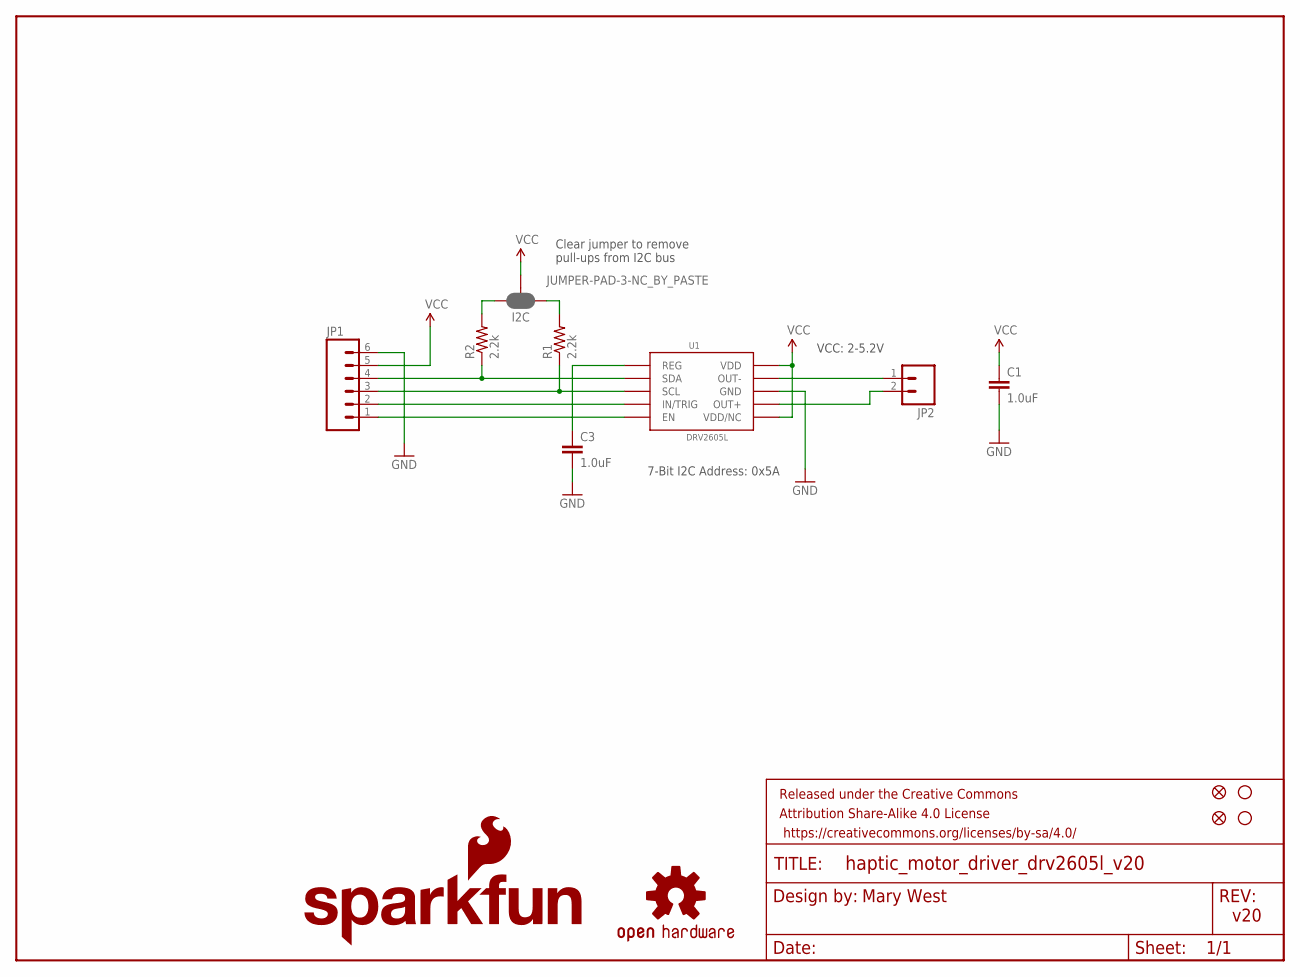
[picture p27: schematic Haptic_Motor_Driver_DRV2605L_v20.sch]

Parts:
C1, C3: 1.0uF; 0402-CAP
FID1, FID2: FIDUCIAL1X2; FIDUCIAL-1X2
FRAME2: FRAME-LETTER; CREATIVE_COMMONS
I2C: JUMPER-PAD-3-NC_BY_PASTE; PAD-JUMPER-3-NC_BY_PASTE_YES_SILK_FULL_BOX
JP1: M06SILK_FEMALE_PTH; 1X06
JP2: M02PTH; 1X02
LOGO2: OSHW-LOGOS; OSHW-LOGO-S
LOGO4: SFE_LOGO_NAME_FLAME.1_INCH; SFE_LOGO_NAME_FLAME_.1
R1, R2: 2.2k; 0603-RES
STANDOFF1, STANDOFF4: STAND-OFF
U1: DRV2605L; VSSOP-10

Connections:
GND: C1.2, C3.2, JP1.6, U1.P$8 (GND)
unnamed: JP1.4, R2.1, U1.P$3 (SDA)
unnamed: JP1.3, R1.1, U1.P$2 (SCL)
unnamed: C3.1, U1.P$1 (REG)
unnamed: JP1.2, U1.P$4 (IN/TRIG)
unnamed: JP1.1, U1.P$5 (EN)
unnamed: JP2.1, U1.P$9 (OUT-)
unnamed: JP2.2, U1.P$7 (OUT+)
unnamed: I2C.3, R2.2
unnamed: I2C.1, R1.2
VCC: C1.1, I2C.2, JP1.5, U1.P$6 (VDD/NC), U1.P$10 (VDD)

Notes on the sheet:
7-Bit I2C Address: 0x5A
VCC: 2-5.2V
Clear jumper to remove pull-ups from I2C bus
v20
Mary West

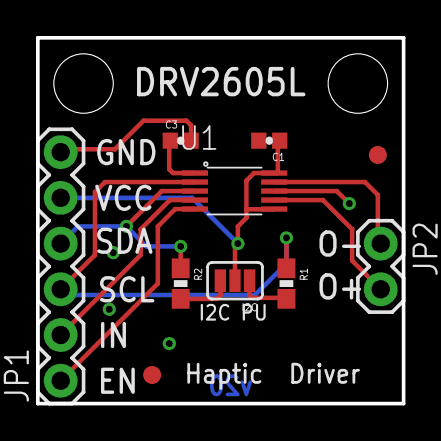
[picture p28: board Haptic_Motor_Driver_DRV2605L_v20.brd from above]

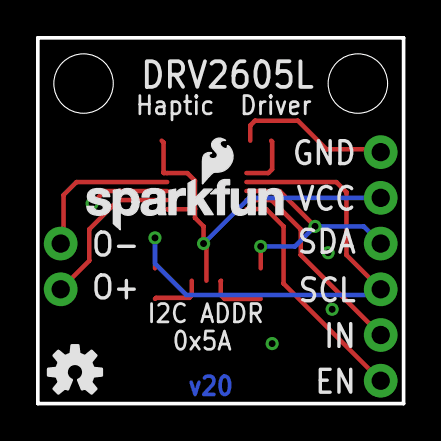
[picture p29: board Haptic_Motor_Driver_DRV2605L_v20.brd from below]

Board: 2 copper layers, 20.3 x 20.3 mm, 15 parts (2 on the bottom side), 11 nets.

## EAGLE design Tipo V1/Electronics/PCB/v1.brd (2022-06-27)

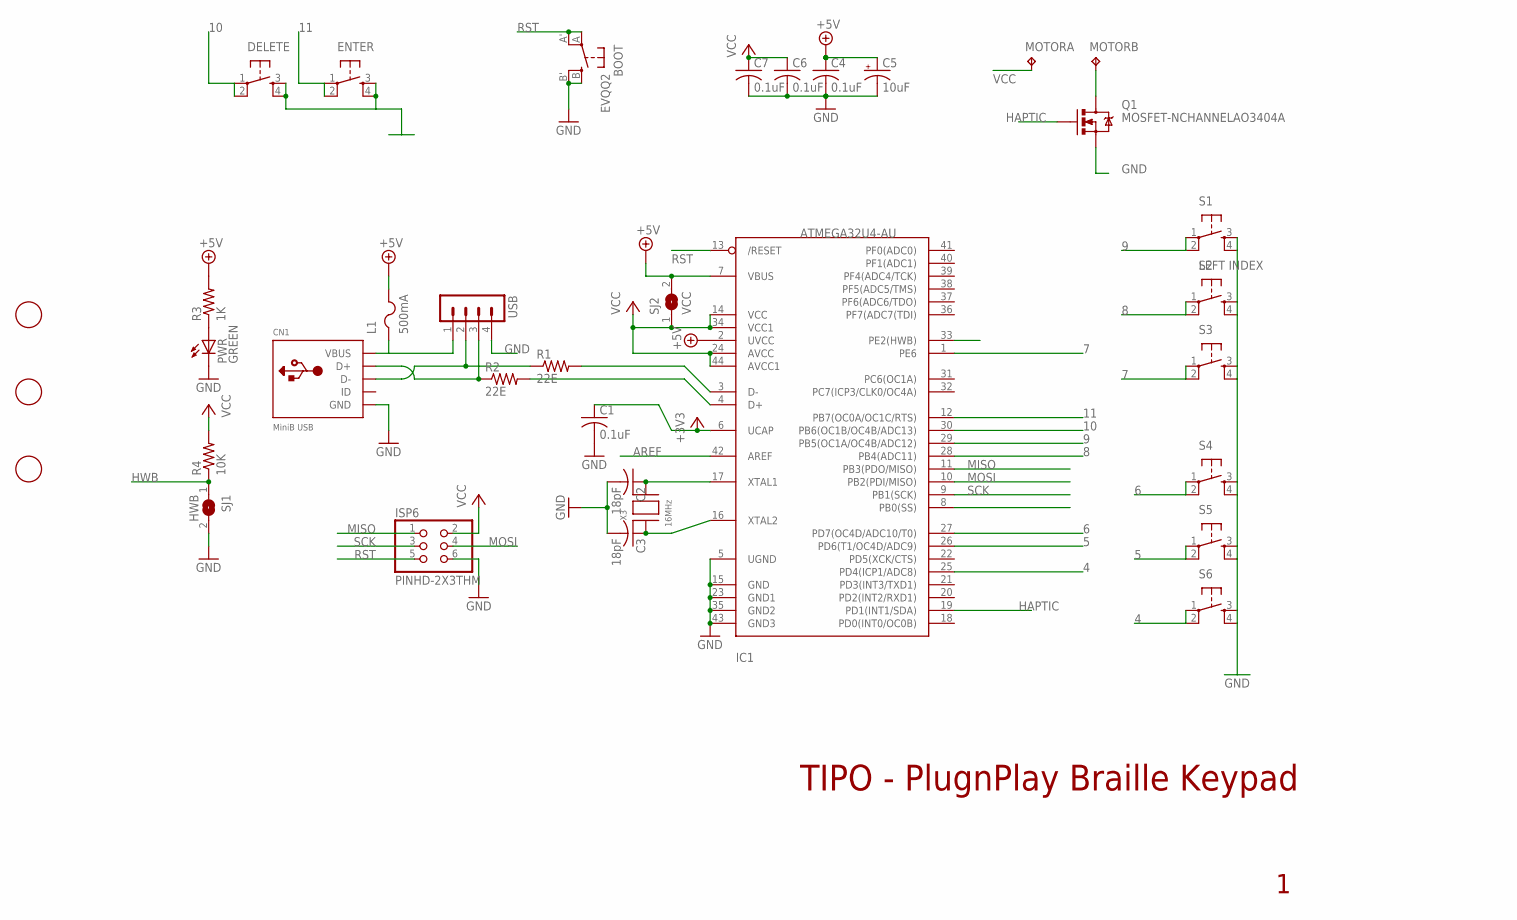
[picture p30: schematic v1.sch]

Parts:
BOOT: EVQQ2; EVQ-Q2
C1, C4, C6, C7: 0.1uF; C0805K
C2, C3: 18pF; C0805K
C5: 10uF; A/3216-18R
CN1: MiniB USB; USB-MINIB
DELETE: TAC_SWITCHPTH; TACTILE-PTH
ENTER: TAC_SWITCHPTH; TACTILE-PTH
IC1: ATMEGA32U4-AU; TQFP44
ISP6: PINHD-2X3THM; ISP6
L1: 500mA; R1206
MOTOR: TP2P2-38-17; P2-38-17
PWR: GREEN; CHIPLED_0805
Q1: MOSFET-NCHANNELAO3404A; SOT23-3
R1, R2: 22E; R0805
R3: 1K; R0805
R4: 10K; R0805
S1: LEFT INDEX; TACTILE-PTH
S2, S3, S4, S5, S6: TAC_SWITCHPTH; TACTILE-PTH
SJ1: HWB; SJ
SJ2: VCC; SJ
U$1, U$2, U$6: FIDUCIAL; FIDUCIAL_1MM
USB: MA04-1
X3: 16MHz; NX5032

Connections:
4: IC1.25 (PD4(ICP1/ADC8)), S6.1, S6.2
5: IC1.26 (PD6(T1/OC4D/ADC9)), S5.1, S5.2
6: IC1.27 (PD7(OC4D/ADC10/T0)), S4.1, S4.2
7: IC1.1 (PE6), S3.1, S3.2
8: IC1.28 (PB4(ADC11)), S2.1, S2.2
9: IC1.29 (PB5(OC1A/OC4B/ADC12)), S1.1, S1.2
10: DELETE.1, DELETE.2, IC1.30 (PB6(OC1B/OC4B/ADC13))
11: ENTER.1, ENTER.2, IC1.12 (PB7(OC0A/OC1C/RTS))
+3V3: C1.1, IC1.6 (UCAP)
+5V: C4.1, C5.+, IC1.2 (UVCC), IC1.7 (VBUS), L1.2, R3.2, SJ2.2
AREF: IC1.42 (AREF)
GND: BOOT.B (S), BOOT.B' (S1), C1.2, C2.2, C3.2, C4.2, C5.-, C6.2, C7.2, CN1.GND, DELETE.3, DELETE.4, ENTER.3, ENTER.4, IC1.5 (UGND), IC1.15 (GND), IC1.23 (GND1), IC1.35 (GND2), IC1.43 (GND3), ISP6.6, PWR.C, Q1.2 (S), S1.3, S1.4, S2.3, S2.4, S3.3, S3.4, S4.3, S4.4, S5.3, S5.4, S6.3, S6.4, SJ1.2, USB.4
HAPTIC: IC1.19 (PD1(INT1/SDA)), Q1.1 (G)
HWB: IC1.33 (PE2(HWB)), R4.1, SJ1.1
MISO: IC1.11 (PB3(PDO/MISO)), ISP6.1
MOSI: IC1.10 (PB2(PDI/MISO)), ISP6.4
unnamed: PWR.A, R3.1
unnamed: CN1.D+, R2.1, USB.3
unnamed: IC1.3 (D-), R1.2
unnamed: IC1.4 (D+), R2.2
unnamed: CN1.D-, R1.1, USB.2
unnamed: MOTOR.TP-2, Q1.3 (D)
unnamed: C2.1, IC1.17 (XTAL1), X3.P$2
unnamed: C3.1, IC1.16 (XTAL2), X3.P$1
PB0: IC1.8 (PB0(SS))
RST: BOOT.A, BOOT.A' (P1), IC1.13 (/RESET), ISP6.5
SCK: IC1.9 (PB1(SCK)), ISP6.3
VBUS: CN1.VBUS, L1.1, USB.1
VCC: C6.1, C7.1, IC1.14 (VCC), IC1.24 (AVCC), IC1.34 (VCC1), IC1.44 (AVCC1), ISP6.2, MOTOR.TP-1, R4.2, SJ2.1

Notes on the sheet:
TIPO - PlugnPlay Braille Keypad

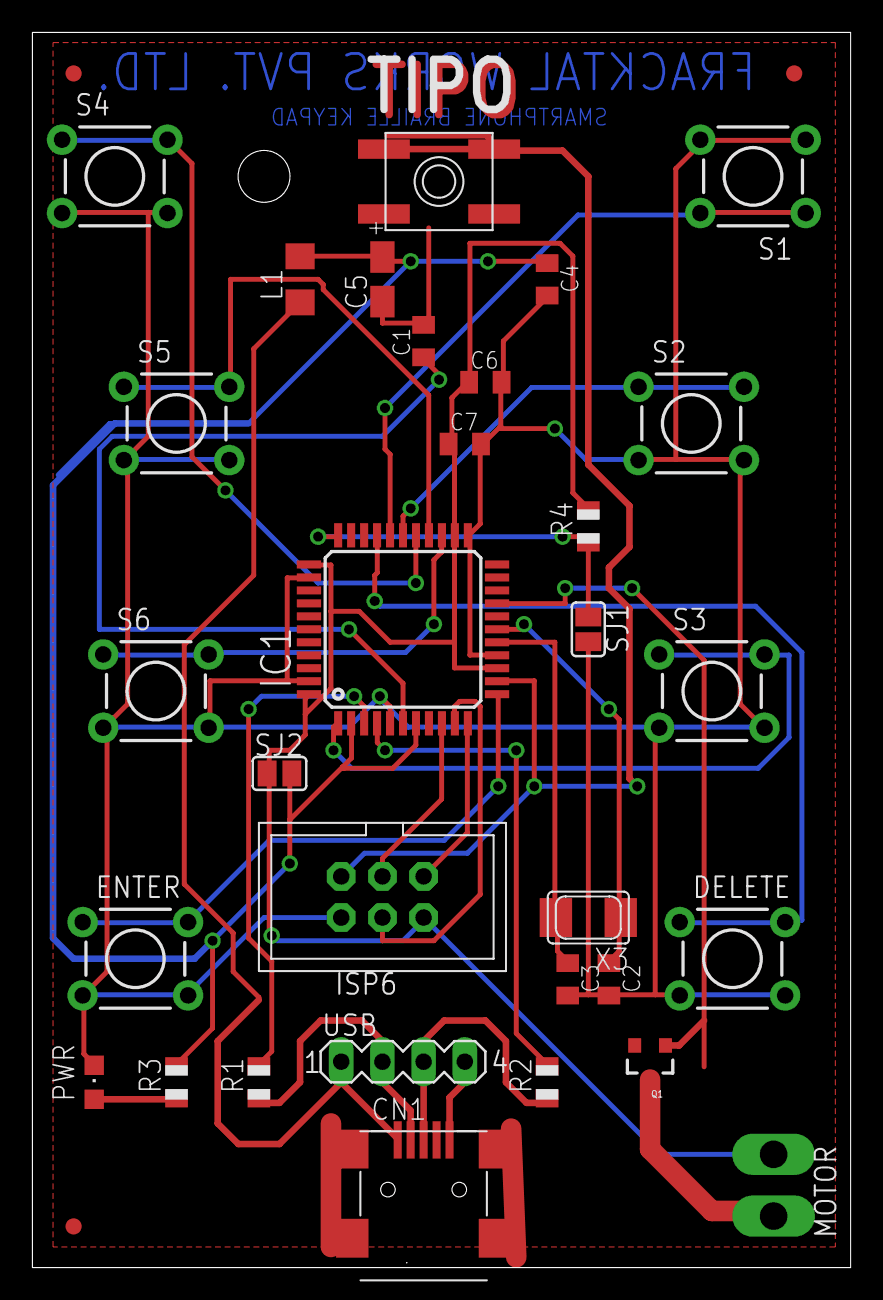
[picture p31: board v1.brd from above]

Board: 2 copper layers, 50.5 x 76.2 mm, 34 parts (0 on the bottom side), 27 nets.

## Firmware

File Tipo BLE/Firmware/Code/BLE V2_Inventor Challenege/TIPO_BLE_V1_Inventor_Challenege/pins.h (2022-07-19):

// #define BTN1 22
// #define BTN2 25
// #define BTN3 14
// #define BTN4 19
// #define BTN5 26
// #define BTN6 27
// #define BTN7 13
// #define BTN8 12
// #define BTN9 32
// #define BTN10 33
// #define BTN11 39
// #define CNT 15
// #define UP 16
// #define DWN 2
// #define RGT 17
// #define LFT 4
// #define statusLED -1
// #define vibrationMotor -1


// TIPO BLE V1.0 Pin Map
#define BTN1 25
#define BTN2 26
#define BTN3 27
#define BTN4 13
#define BTN5 15
#define BTN6 2
#define BTN7 19
#define BTN8 18
#define BTN9 17
#define BTN10 16
#define BTN11 4
#define CNT 33
#define UP 34
#define DWN 35
#define RGT 39
#define LFT 36
#define statusLED 23
#define vibrationMotor 32

#define braillePinMapArrayLength  (sizeof(braillePinMap) / sizeof(braillePinMap[0]))
#define functionPinMapArrayLength  (sizeof(functionPinMap) / sizeof(functionPinMap[0]))
#define grade1CharMapArrayLength (sizeof(grade1CharMap) / sizeof(grade1CharMap[0]))
#define grade1PunctuationMapArrayLength (sizeof(grade1PunctuationMap) / sizeof(grade1PunctuationMap[0]))
#define numMapArrayLength (sizeof(numMap) / sizeof(numMap[0]))
#define grade1CapCharMapArrayLength (sizeof(grade1CapCharMap) / sizeof(grade1CapCharMap[0]))
#define symbolMapArrayLength (sizeof(symbolMap) / sizeof(symbolMap[0]))
#define alphabeticWordsignsMapArrayLength (sizeof(alphabeticWordsignsMap) / sizeof(alphabeticWordsignsMap[0]))
#define strongContractionsMapArrayLength (sizeof(strongContractionsMap) / sizeof(strongContractionsMap[0]))
#define strongGroupsignsMapArrayLength (sizeof(strongGroupsignsMap) / sizeof(strongGroupsignsMap[0]))
#define shortformWordsMapArrayLength (sizeof(shortformWordsMap) / sizeof(shortformWordsMap[0]))
#define initialLetterContractionsMapArrayLength ((sizeof(initialLetterContractionsMap) / sizeof(initialLetterContractionsMap[0])))
#define strongWordsignsMapArrayLength (sizeof(strongWordsignsMap) / sizeof(strongWordsignsMap[0]))
#define finalLetterGroupsignsMapArrayLength (sizeof(finalLetterGroupsignsMap) / sizeof(finalLetterGroupsignsMap[0]))
#define lowerGroupsigns_joining_MapArrayLength ((sizeof(lowerGroupsigns_joining_Map) / sizeof(lowerGroupsigns_joining_Map[0])))
#define lowerGroupsigns_starting_MapArrayLength ((sizeof(lowerGroupsigns_starting_Map) / sizeof(lowerGroupsigns_starting_Map[0])))

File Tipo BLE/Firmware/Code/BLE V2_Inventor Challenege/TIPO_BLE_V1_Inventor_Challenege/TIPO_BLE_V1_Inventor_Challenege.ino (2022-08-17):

unsigned int longPressTime = 1000;
int bounceTime = 50;

#include <BleKeyboard.h> //https://github.com/T-vK/ESP32-BLE-Keyboard
BleKeyboard  bleKeyboard(" BraillePad", "Vijay", 100);

#include "pins.h"
#include "readButtons.h"
#include "grade1Braille.h"
#include "grade2Braille.h"
#include "shortcuts.h"
#include "processButtons.h"



void setup() {
  for (int i = 0; i < braillePinMapArrayLength; i++)
  {
    pinMode(braillePinMap[i], INPUT_PULLUP);
  }
  for (int i = 0; i < functionPinMapArrayLength; i++)
  {
    pinMode(functionPinMap[i], INPUT_PULLUP);
  }
  pinMode(vibrationMotor, OUTPUT);
  pinMode(statusLED, OUTPUT);
  digitalWrite(statusLED, HIGH);
  digitalWrite(vibrationMotor, HIGH);
  delay(100);
  digitalWrite(vibrationMotor, LOW);
  digitalWrite(statusLED, LOW);

  Serial.begin(115200);
  bleKeyboard.begin();
}


void loop() {
  if (bleKeyboard.isConnected()) {
    if (isBrailleButtonPressed())
      processBrailleButtonState(getbrailleButtonState());
    if (isFunctionKeyPressed())
      processFunctionButtonState(getFunctionButtonState());
    // Serial.println();
    // Serial.print("Typed Word = ");
    // Serial.print(typedWord);
    // Serial.print(" inputBeforePrevInput= ");
    // Serial.print(inputBeforePrevInput,BIN);
    // Serial.print(" prevInput= ");
    // Serial.print(prevInput,BIN);
    delay(bounceTime);
  }
}


/*
  TO DO
  Shortcuts
  lower wordsigs and groupsigns
  battery level vibration
  battery level to phone
  BT pair mode on/off
*/

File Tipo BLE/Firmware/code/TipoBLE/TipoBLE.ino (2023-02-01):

#define DEBUG 1
#include <BleKeyboard.h> //https://github.com/T-vK/ESP32-BLE-Keyboard

BleKeyboard  bleKeyboard("Braille keyboard", "Vijay", 100);

int bouncetime = 50;
//               s6,s5,s4,s3,s2,s1,Space,DEL,Enter,Esc,UP,DOWN,LEFT,RIGHT)
byte pinMap[] = {27 , 26, 19, 14, 25, 22, 13, 12,32,33,15,16,2,4,17};
int arraySize =  (sizeof(pinMap) / sizeof(pinMap[0]));
byte keyMap[] = {
  B000000,
  'a', B00100000,//a
  'b', B00110000,
  'c', B00100100,
  'd', B00100110,
  'e', B00100010,
  'f', B00110100,
  'g', B00110110,
  'h', B00110010,
  'i', B00010100,
  'j', B00010110,
  'k', B00101000,
  'l', B00111000,
  'm', B00101100,
  'n', B00101110,
  'o', B00101010,
  'p', B00111100,
  'q', B00111110,
  'r', B00111010,
  's', B00011100,
  't', B00011110,
  'u', B00101001,
  'v', B00111001,
  'w', B00010111,
  'x', B00101101,
  'y', B00101111,
  'z', B00101011, //z
  '#', B00001111,
  ' ', B00001001,
};

char ch;

/* 
Function that reads the combination of pressed buttons.Only if a button is pressed and
subsequently released would the function return a value.
input: byte array of all the physical pin numbering in the sequence s6,s5,s4,s3,s2,s1,SPACE,DEL
Returns: charecter or function button
*/
byte readKeys() {
  byte fullCharKeyValue = B00000000; //initial value for charecter key combination
  byte singleCharKeyValue = B00000000; //initial value for single button press for charecter key
  byte functionKeyValue = B10000000; //initial value for function key combination
  while (1) {  //run in a loop
    singleCharKeyValue = 0; //reset back to zero after every loop
    for (int i = 0; i < 6; i++) 
    { //read all charecter buttons in a sequence
      if (digitalRead(pinMap[i]) == LOW) 
      {//Enter 1 in the apropriate position for each charter button combination in the byte
        singleCharKeyValue = 1;
        singleCharKeyValue <<= i; //bitshift left https://www.arduino.cc/reference/en/language/structure/bitwise-operators/bitshiftleft/
        fullCharKeyValue = fullCharKeyValue | singleCharKeyValue; //Bitwise or https://www.arduino.cc/reference/en/language/structure/bitwise-operators/bitwiseor/
        delay(bouncetime);
        //if (DEBUG)Serial.println(fullCharKeyValue, BIN);
      }
    }
    if (!singleCharKeyValue && fullCharKeyValue) //only when X goes back to 0, return the last known values of a, but untill then keep updating a
    {
      delay(3* bouncetime);
      return fullCharKeyValue;
    }
    if (!fullCharKeyValue) //if none of the character buttons were pressed, check for function keys
      for (int i=6; i<15; i++)
      {
        if (digitalRead(pinMap[i]) == LOW)
        {
          functionKeyValue = B10000000;
          functionKeyValue += i;
          return functionKeyValue;
        }
      }
  }
}

char convert(byte keys) {
  for (int i = 0; i <= 56; i += 2) {
    if (keyMap[i] == keys)
      return keyMap[i - 1];
  }
  return 0;
}


/*
Function that reads the byte  value and returns a charector or function to perform
input: byte value of charecr keys or functions
output: char
*/
char processKeys(byte keyValue)
  {
    Serial.println(keyValue,BIN);
    char c = convert(keyValue);
    if (keyValue < B10000000) //Not a fucntion key press
    {
      if (c != '#')  //Not a number
        //return c;
         bleKeyboard.write(c);
      else
      {  label:
         keyValue= readKeys();
         if (convert(keyValue) == '#' or keyValue== 0)
          goto label;
        //keys = readKeys(pinMap[], bouncetime);
       // c = convert(keys) - 16;//ascii conversion from A to 1, B to 2 etc
         c = (convert(keyValue) - 48);//ascii conversion from A to 1, B to 2 etc
         Serial.println(c);
        if (c == 58) c = '0'; //0 after 9 not before 1 in braille alphabet
        //return c;
        bleKeyboard.write(c);
      }
    }
    else
    {
      switch (keyValue)
      {
        case B10000111:
        bleKeyboard.write(KEY_BACKSPACE);
        delay(100);
        break;
        case B10000110:
        bleKeyboard.write(' ');
        delay(100);
        break;
        case B10001000:
        bleKeyboard.write(KEY_ESC);
        delay(100);
        break;
        case B10001001:
        bleKeyboard.write(KEY_RETURN);
        delay(100);
        break;
        case B10001100:
        bleKeyboard.write(KEY_UP_ARROW);
        delay(100);
        break;
        case B10001010:
        bleKeyboard.write(KEY_DOWN_ARROW);
        delay(100);
        break;
        case B10001101:
        bleKeyboard.write(KEY_LEFT_ARROW);
        delay(100);
        break;
        case B10001011:
        bleKeyboard.write(KEY_RIGHT_ARROW);
        delay(100);
        break;
        case B10001110:
        bleKeyboard.write(KEY_TAB);
        delay(100);
        break;
      }
    }
  }


  void setup(){
  for (int i = 0; i< arraySize; i++)
  {
    pinMode(pinMap[i],INPUT_PULLUP);
  }
  Serial.begin(115200);
  Serial.println("Starting BLE work!");
  bleKeyboard.begin();
  }

  void loop(){
    if(bleKeyboard.isConnected()) {
      processKeys(readKeys());
//      ch = processKeys(readKeys());
//      if (ch)
//      {
//       bleKeyboard.write(ch);
//       ch = 0;
//      }
        delay(100);
        bleKeyboard.releaseAll();
      }
   
  }

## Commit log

2022-06-22 Synced CAD parts
    [Button Head.ipt, Clampshell Body Top.0002.ipt, Clampshell Body Top.ipt, Clampshell Body Top.stl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]
2022-06-27 Organized the folder
    [Button Head.ipt, Clampshell Body Top.0002.ipt, Clampshell Body Top.ipt, Clampshell Body Top.stl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]
2022-07-04 Documentation Updated
    [Button List.xlsx]
2022-07-07 Synced board files, updated documentation
    [EPS32THINGY.brd, EPS32THINGY.sch, Haptic_Motor_Driver_DRV2605L_v20.brd, Haptic_Motor_Driver_DRV2605L_v20.sch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]
2022-07-07 Fixed silk screen on bottom layer
    [TIPO BLE.brd, TIPO BLE.sch]
2022-07-08 Files updated, Working code
    [5-WayTactileButton10mmSMD.stp, ALPSALPINE SKSGPCE010.SLDPRT, ALPSALPINE SKSGPCE010.STEP, Button Head.ipt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]
2022-07-09 Code updates
    [Back cover.stl, Dome switch retainer.stl, JOtstick.stl, PCB Component.stl]
2023-02-01 Niidhi Prayas
    [Button List.xlsx]

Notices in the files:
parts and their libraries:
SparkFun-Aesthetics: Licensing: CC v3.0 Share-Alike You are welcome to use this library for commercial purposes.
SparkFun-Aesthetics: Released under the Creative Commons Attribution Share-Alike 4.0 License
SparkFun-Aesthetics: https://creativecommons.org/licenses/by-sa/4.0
